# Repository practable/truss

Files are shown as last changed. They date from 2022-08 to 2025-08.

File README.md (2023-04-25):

# truss

## Introduction

The truss remote laboratory has been designed for use with Structural Engineering and Engineering Design courses at the University of Edinburgh. The truss consists of 6 members, each with a full-bridge strain gauge arrangement using two biaxial strain gauges ([Kyowa KFGS-2-120-D16-11](./hw/docs/)). Strain gauge voltages are converted to digital signals using the [HX711 ADC](./hw/docs/) and this [HX711 library](https://www.arduino.cc/reference/en/libraries/hx711-arduino-library/) is used to read and tare the gauges. The truss is loaded using a [linear servo](./hw/docs/). 

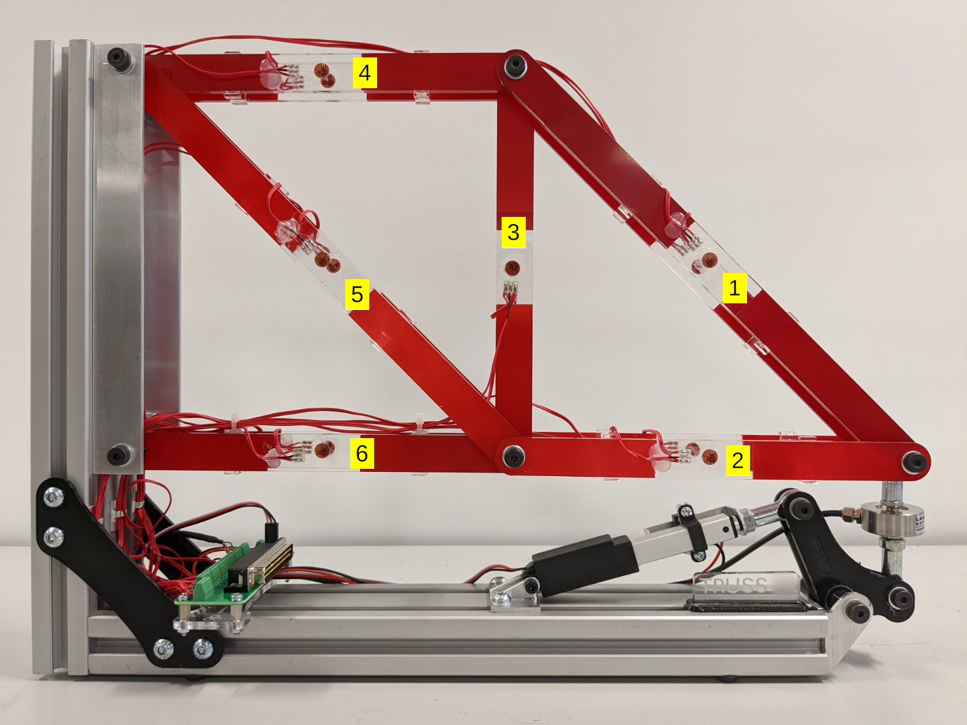
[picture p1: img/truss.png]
truss


## Contents

- [Firmware ./fw](./fw/)
- [Hardware ./hw](./hw/)
- [SBC ./sbc](./sbc/)
- [UI ./ui](./ui/)

## UI

User Interfaces have been designed with Vue3.js and built with Vite. There are currently three distinct versions of the UI ready to build:

- [default](./ui/default/): all data and components available on the user interface.
- [no-force](./ui/no-force/): force data is hidden for student calculation from strain data.
- [open-day](./ui/open-day/): simplified control interface for demonstrations.

## Changing control interface on UI

The differences in the above UI versions amount to very simple changes in the Vue files. 

The load force can be controlled with either a slider or simple buttons (as well experimental versions of a skeuomorphic display and gamepad control). Simply update the `loadControlVersion` parameter in `App.vue`.

```
loadControlVersion: 1,    //0 => input field, 1=> slider, 2=>simulation of physical knob, 3 => direct commands typed, 4 => GamePad, 5 => open day, simple buttons
```

To change whether the load force is displayed or the theoretical strains are available, update the boolean parameters in `src/modules/uiStore.js`:

```
show_force: false,       //should force values be displayed on the UI
show_theory: false,      //should the theoretical values component be available on the UI
```

## Firmware

The truss remote lab has been designed around the Arduino Nano 33 IoT. The firmware uses a state machine with 11 states, including reading, writing, taring and resetting strain gauges and moving the linear actuator. A single microcontroller performs both reading and writing of data. The state machine will remain in the READ state until a user command to change state. Upon performing that state the state machine will return to READ. The required libraries are included [here](./fw/libraries/). 

The firmware sends and receives JSON messages, eg:

Mode control, received from UI through Serial (for all commands see [SerialCommands](./fw/MiniTruss/):

```
{"set": "position", "to": value} 
{"set": "mode", "to": "move"} 
{"set": "mode", "to":"tare_all"} 
```

Sending data to UI through Serial:
```
{"load_cell":"20.0", "gauge_1": "100.0", "gauge_2": "100.0", "gauge_3": "100.0", "gauge_4": "100.0", "gauge_5": "100.0", "gauge_6": "100.0", "state":"1", "pos":"10"}
```

## PCB

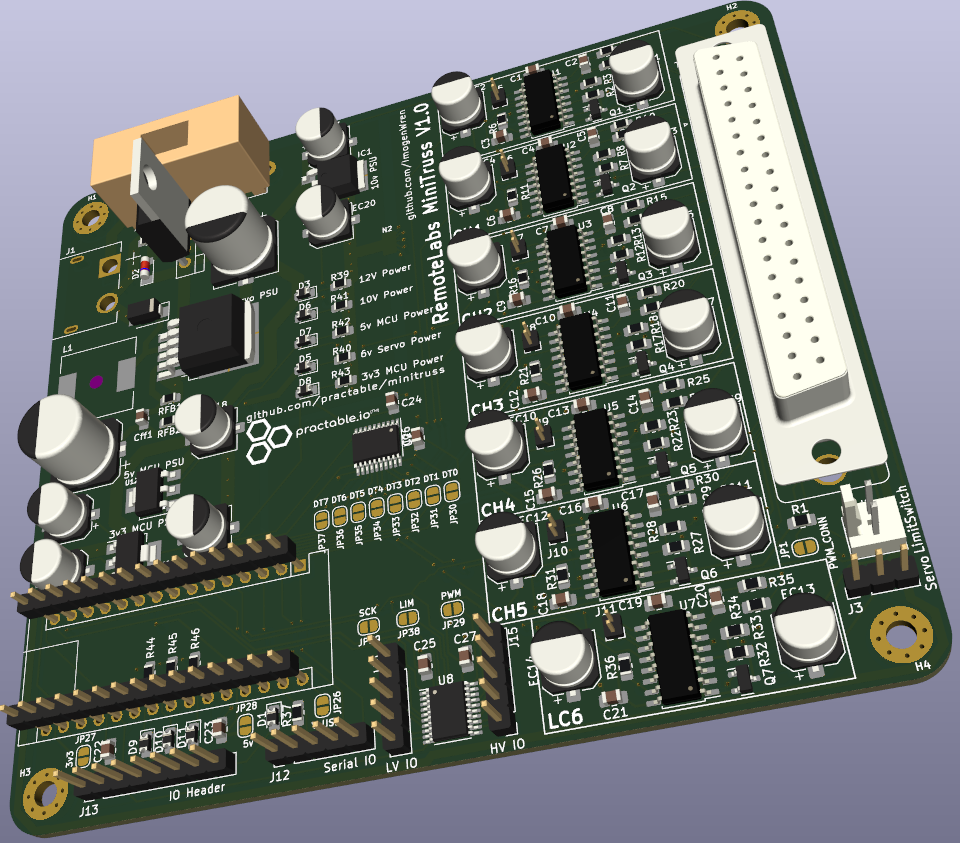
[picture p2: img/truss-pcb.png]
truss-pcb


The PCB requires a 12V input and provides output voltages for different components: 10V (load cell excitation voltage), 6V (linear actuator power) and 5V (strain gauge excitation voltage). Details of jumper requirements for setting up the PCB in different modes will be added (TODO).

## Hardware

linear-actuator

The [Actuonix L16](./hw/docs/Actuonix+L16+Datasheet.pdf) linear actuator uses the custom library LinearServo for setting its position. It has a 50mm stroke length, but is limited in this remote lab to a maximum of 20% extension (providing around 150N of load on the truss).

## Re-calibration procedure

If a strain gauge value no longer reads an acceptable result (within your experimental tolerance) then the scale factor needs to be updated in the firmware.

- Note the value in micro-strain that the gauge is currently reading (current_value)
- Note the current scale factor for that gauge (current_factor)
- Calculate the value that you want it to read based on the load force (new_value)
- new_factor = current_value*current_factor / new_value

Using the debug UI (or any other means of sending a JSON command through Websocket to the experiment): send the new calibration data:

```
{"set":"cal","to":[2.0,2.1,2.2,2.3,2.4,2.5,2.6],"auth":"foo"}
```

Using the auth code that you set up initially.

Then reset to the STARTUP state so that the firmware loads the new calibration data:

```
{"set":"state","to":"STATE_STARTUP"}
```

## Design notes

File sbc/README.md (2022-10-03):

# odroid-truss
How to set up an Odroid to run a truss experiment. 

The process is fairly simple
0. Obtain an eMMC card with Ubuntu 20.04 LTS 
0. Connect Odroid to power, network and a Nano IoT33 
0. Log in to check you have ssh access
0. Edit the sudoers file to allow passwordless sudo
1. Run a configure script on your admin machine
2. Run four ansible playbooks on your admin machine (which set things up on the rpi over ssh)
3. Reboot your Odroid
3. Your experiment should be working

## Abbreviations

- BYOD - Bring Your Own Device
- OS - Operating System
- SBC - single board computer (Raspberry Pi, Odroid, etc)

## Formatting

### Trimming information

`<snip>` is used to denote that line(s) have been removed for clarity

```
something useful
<snip>
other useful stuff
```

#### repo location

`$this_repo` is used to indicate the root of the git repo for clarity in the documentation, and does not actually occur in any of the scripts.

### Indicating where to enter commands?

Code snippets will sometimes clarify which machine they should be run on, if it is not obvious from the context. E.g. your local admin machine:
```
# local
$ <some commands>
```

or on the SBC (via the ssh connection you've established from your local machine). 

```
# sbc
$ <some command>
```

## Prequisites

### Hardware

This is our tested configuration. 

- Odroid C4 
- 32GB eMMC preloaded with ubuntu 20.04 LTS (or a blank eMMC and an adapter so you can image it)
- USB A to micro B cable for arduino
- Arduino Nano IOT33
- USB Webcam (Logitech C920)
- 12V power supply with barrel jack connector
- RJ45 Ethernet connection (avoid WiFi because it is laggy for users)
	
For assembling the full experiment, you will also need some additional items that are outside the scope of this repo:
- Truss PCBs including sensor and connector boards
- Truss hardware (truss, guages, actuator, load cell)
- Experimental tray and 1/6th scale shipping container

### Software

The setup is best done from a linux machine. We have no plans to support commercial operating systems.

- Linux 
   - recommend Ubuntu 20.04 LTS
- Practable's [relay](https://github.com/practable/relay) 
    - ensure the `sessionrelay` and `shellrelay` commands are in your path
    - you may need to rename the commands from `session` to `sessionrelay`, and `shell` to `shellrelay` when you copy them to `/usr/local/bin'.
- Mo templating in bash 
    - see [github](https://github.com/tests-always-included/mo) for installation
    - there are other ways to get mo (e.g. with python) but we don't know if they work, so avoid for now.
- Ansible 
   - Tasks developed with v2.9.17 and python 3.7.4
   - [Installation](https://docs.ansible.com/ansible/latest/installation_guide/intro_installation.html)

### Information

You will need either access tokens or the access secret(s) to your relay(s). Your site administrator for practable will advise. These scripts are written for the case you have the secret. If you have been provided some tokens, you just copy them into `$this_repo/autogenerated` and skip some steps where indicated.

We assume that your relay access secret is the same for all the relays in use, and available at `~/secret/practable.pat`. That way, it's not in the repo.

### Network

You need a wired staging network where unknown devices can obtain an IP address via DHCP. Your admin machine is ideally also in the same subnet as your RPI. If you are at work/university, then you will need to create your own staging network because most institutional networks prevent unknown devices from accessing the wired networks. Without a staging network, you are are stuck in a catch-22 of not knowing enough about the device to get that permission for access to the production network (typically a BYOD network for devices that staff and students might bring in).

Good staging networks: your home network (no re-configuration is needed) or a linux laptop with a wifi connection and an RJ45 dongle (share the wifi to the dongle) - I use one for initial setups and the other for ad-hoc direct connections to experiments during field-testing.

### User environment

#### Mandatory

None listed

## Setup

Overview: The process starts by loading an OS onto an SD card, modifying it to permit `ssh` access, then finishing the setup over an ssh connection. There are a mixture of steps conducted on the SBC

### SBC OS

#### Base Image

Obtain a preloaded eMMC with Ubuntu 20.04 LTS, or image this to your blank eMMC. The most likely looking offical distro is [this](https://odroid.in/ubuntu_22.04lts/C4_HC4/ubuntu-22.04-4.9-minimal-odroid-c4-hc4-20220705.img.xz).  

SSH is enabled by default.

#### Find the IP address of your SBC

Before booting your SBC, you need to figure out the IP addresses of other devices on your network. In the next step, we will be looking for the IP address of the SBC, and it is easier if you already know which devices are NOT the SBC.

First, let's figure out the IP address of the wired ethernet port on your admin machine 
```
$ ip addr 
<snip>
3: enp0s31f6: <BROADCAST,MULTICAST,UP,LOWER_UP> mtu 1500 qdisc fq_codel state UP group default qlen 1000
    link/ether xx:xx:xx:xx:xx:xx brd ff:ff:ff:ff:ff:ff
    inet 192.168.0.46/24 brd 192.168.0.255 scope global dynamic noprefixroute enp0s31f6
       valid_lft 784687sec preferred_lft 784687sec
    inet6 xxxx::xxxx:xxxx:xxxx:xxxx/64 scope link noprefixroute 
       valid_lft forever preferred_lft forever
<snip>
```
Our network card is at 192.168.0.46. The first three number groups matter here. Find all the devices on the same sub-net, using that IP address by set the last number group to `1/24` which is [shorthand](https://www.ietf.org/rfc/rfc1878.txt) for 0-254 (all possible IP in the subnet).
```
$ sudo nmap -sP 192.168.0.1/24
sudo nmap -sP 192.168.0.1/24
Starting Nmap 7.80 ( https://nmap.org ) at 2022-08-25 13:18 BST
Nmap scan report for _gateway (192.168.0.1)
Host is up (0.0016s latency).
MAC Address: xx:xx:xx:xx:xx:xx 
Nmap scan report for 192.168.0.62
Host is up (0.00059s latency).
MAC Address: xx:xx:xx:xx:xx:xx 
Nmap scan report for 192.168.0.52
Host is up (0.036s latency).
MAC Address: xx:xx:xx:xx:xx:xx 
Nmap scan report for 192.168.0.184
Host is up (0.00027s latency).
Nmap done: 256 IP addresses (3 hosts up) 
```

Put the eMMC card on your Odroid, connect the network cable, and power on. Wait about a minute (or repeat until a new device shows up)

```
$ sudo nmap -sP 192.168.0.1/24
sudo nmap -sP 192.168.0.1/24
Starting Nmap 7.80 ( https://nmap.org ) at 2022-08-25 13:20 BST
Nmap scan report for _gateway (192.168.0.1)
Host is up (0.0016s latency).
MAC Address: yy:yy:yy:yy:yy:yy (Arris Group)
Nmap scan report for 192.168.0.29
Host is up (0.032s latency).
MAC Address: xx:xx:xx:xx:xx:xx 
Nmap scan report for 192.168.0.62
Host is up (0.00059s latency).
MAC Address: xx:xx:xx:xx:xx:xx 
Nmap scan report for 192.168.0.52
Host is up (0.036s latency).
MAC Address: xx:xx:xx:xx:xx:xx 
Nmap scan report for 192.168.0.184
Host is up (0.00027s latency).
Nmap done: 256 IP addresses (4 hosts up) 
```
Now you should see a new device. If this step does not work, then the eMMC is corrupt, the network cable/power are disconnected, or the router on your network is not permitting DHCP requests from unknown devices.

In this case the IP address is 192.168.0.29.

Make a note of the MAC address of your SBC so that you can share that with your network administrators at the University - sometimes you must declare the MAC address to be able to access a wired BYOD network.

#### ssh into your SBC

The standard user and password on the odroid image is usually `odroid/odroid`

On your machine, open a terminal
```
$ ssh pi@192.168.0.29 #change to whatever IP you found in previous step

The authenticity of host '192.168.0.29 (192.168.0.29)' can't be established.
ECDSA key fingerprint is SHA256:/0jZ9w8zL4h94rojSnSQ0Yewv5G8qK2AjCod/09pBkE.
Are you sure you want to continue connecting (yes/no/[fingerprint])? yes
Warning: Permanently added '192.168.0.29' (ECDSA) to the list of known hosts.
pi@192.168.0.29's password: <--- enter the password here 

```
Then you should see something like this:

```
Welcome to Ubuntu 20.04 LTS (GNU/Linux 4.9.218-13 aarch64)

 * Documentation:  https://help.ubuntu.com
 * Management:     https://landscape.canonical.com
 * Support:        https://ubuntu.com/advantage

 * Super-optimized for small spaces - read how we shrank the memory
   footprint of MicroK8s to make it the smallest full K8s around.

   https://ubuntu.com/blog/microk8s-memory-optimisation

607 updates can be installed immediately.
426 of these updates are security updates.
To see these additional updates run: apt list --upgradable

Last login: Fri Jul  1 20:11:11 2022 from 192.168.0.46
odroid@odroid:~$  
```

##### Password

Change the password 

```
$ passwd
```

Ideally we would also set up ssh certificates but this is a future step.

##### Sudo

Set up passwordless sudo

```
#sbc
sudo visudo 
```

At the end of the file add

```
odroid ALL=(ALL) NOPASSWD: ALL
```

Save the file. The default editor might be joe, in which case you hit `^KX` (i.e. hold CTRL, type KX, release CTRL) to save. Assuming you made no errors, you will see:

```
File /etc/sudoers.tmp saved
```

Once the sudoers file is edited, you can check it by logging back out and back in, then trying 

```
$ sudo su
root@odroid:/home/odroid# 
```

which should work without needing a password.

You can now exit the session - we will do the next steps using ansible.

```
# sbc
$ exit
```

### SBC software and configuration

We need to generate some configuration files that are customised to your experiment. Your local admin for the practable system will advise on any naming conventions that apply at your site, as well as providing the relay key(s) which you need. 

#### Ansible hosts file

We need to let ansible know about this host.

```
sudo nano /etc/ansible/hosts
```
Add in a section like this (or modify an existing section if you have one)

```
<snip>
[truss]
trus00 ansible_host=192.168.0.29 practable_label=trus00

[truss:vars]
ansible_connection=ssh
ansible_user=odroid
ansible_password=somepassword
<snip>

```

#### Practable connections

We need to configure routing and tokens for the video, data, shell, and shell2 connections. There are scripts provided to help you. They put files into `$this_repo./autogenerated`

Create the configuration files we need, assuming we are using the standard practable relay URLs.

```
#local
cd scripts
./configure trus 00 00 https://relay-access.practable.io https://shell-access.practable.io https://shell-access2.practable.io
```

##### Session

Now we can run our ansible playbooks - these each take some time, so get the kettle ready. It's nearly as fast doing multiple machines, because the playbooks are run in parallel. There is no need to do each SBC separately one after another.

```
#local
cd playbooks
ansible-playbook prepare.yml
ansible-playbook install-session.yml
ansible-playbook install-shell.yml
ansible-playbook install-firmware.yml
```

If those commands go smoothly, then you are done with the install. If not, then re-run the playbook with the issue, before moving on. If that fails, check out the troubleshooting guide below.

## Checking the installation

Go to the booking page link the adminstrator gave you, and you should be able to access/control the experiment. 

## Troubleshooting

If things are not working right, then you might be able to fix them by troubleshooting. 

### First playbook fails

If you get this error, just redo the playbook. It's down to the python interpreter not being picked up after installation in a previous step.

```
TASK [Remove any existing go files] *******************************************************************************************************************
fatal: [trus02]: FAILED! => {"changed": false, "module_stderr": "/bin/sh: 1: /usr/bin/python: not found\n", "module_stdout": "", "msg": "The module failed to execute correctly, you probably need to set the interpreter.\nSee stdout/stderr for the exact error", "rc": 127}
```

### No DHCP

This is usually caused by 
- eMMC corrupt 
- network administrator is unaware of the MAC address of the wired network port on the SBC

### No SSH connection

For odroid, `sshd` is enabled by default, so you will need to use a keyboard and mouse to re-enable, or reflash (depending on whether there is anything on the eMMC you want to keep).

### Remote host identification has changed

If you work with a lot of experiments, sooner or later an old IP address on your staging network will be re-assigned to a new experiment you are setting up, and then you will see something like this:

```
@@@@@@@@@@@@@@@@@@@@@@@@@@@@@@@@@@@@@@@@@@@@@@@@@@@@@@@@@@@
@    WARNING: REMOTE HOST IDENTIFICATION HAS CHANGED!     @
@@@@@@@@@@@@@@@@@@@@@@@@@@@@@@@@@@@@@@@@@@@@@@@@@@@@@@@@@@@
IT IS POSSIBLE THAT SOMEONE IS DOING SOMETHING NASTY!
Someone could be eavesdropping on you right now (man-in-the-middle attack)!
It is also possible that a host key has just been changed.
The fingerprint for the ECDSA key sent by the remote host is
SHA256:/0jZ9w8zL4h94rojSnSQ0Yewv5G8qK2AjCod/09pBkE.
Please contact your system administrator.
Add correct host key in /home/tim/.ssh/known_hosts to get rid of this message.
Offending ECDSA key in /home/tim/.ssh/known_hosts:178
  remove with:
  ssh-keygen -f "/home/tim/.ssh/known_hosts" -R "192.168.0.184"
ECDSA host key for 192.168.0.184 has changed and you have requested strict checking.
Host key verification failed.
```

Simply run the suggested command, and then carry on where you left off with trying to connect over `ssh`. The command is unique each time it happens (you're overwriting an entry in the known-hosts file so it must correspond to the host causing the problem _this_ time). E.g.

```
$ssh-keygen -f "/home/tim/.ssh/known_hosts" -R "192.168.0.184"

# Host 192.168.0.184 found: line 178
/home/tim/.ssh/known_hosts updated.
Original contents retained as /home/tim/.ssh/known_hosts.old
```

### Check the OS
If you're not sure if you have the right OS for the ansible scripts, you can check. For this experiment, you should see something like this

```
$ uname -a
Linux odroid 4.9.218-13 #1 SMP PREEMPT Tue Apr 21 20:02:01 UTC 2020 aarch64 aarch64 aarch64 GNU/Linux
```

### Ansible cannot reach SBC

If you are having trouble connecting via ansible, following the guidance on verbose logging [here](https://docs.ansible.com/ansible/latest/network/user_guide/network_debug_troubleshooting.html)

You might find you've got the format of the /etc/ansible/hosts incorrect (e.g. didn't name the vars section correctly, got the password wrong etc).

### ttyACM0 Device not found 

If you get this error, reboot the SBC and try again. If the error persists, check which device name it has been assigned (`/dev/ttyACM0` is expected for Nano 33 IOT)
```
#rpi
lsusb
dmesg | tail
```

### Error with sudo / sudoers

If you made an error, you might see something like this
```
>>> /etc/sudoers: syntax error near line 26 <<<
What now? 
```
In which case, hit `e` to go back to the editor and correct the mistake.

#### Direct editing error

Editing the sudoers file directly can lock you out of running commands as sudo, if you make an error. Recovering it is [straightforward](https://askubuntu.com/questions/73864/how-to-modify-an-invalid-etc-sudoers-file).

Ali Tou says:
"When this happens to a non-GUI system (your production server, maybe) the pkexec fails with this error message:

```
polkit-agent-helper-1: error response to PolicyKit daemon: GDBus.Error:org.freedesktop.PolicyKit1.Error.Failed: No session for cookie
==== AUTHENTICATION FAILED ===
Error executing command as another user: Not authorized
```
In this situation, using `pkttyagent` can be helpful. If you want to remove a corrupted file in `sudoers.d` directory, use this:

```
pkttyagent -p $(echo $$) | pkexec rm /etc/sudoers.d/FILENAME
```

If you want to recover the default `/etc/sudoers`, you can use [this gist](https://gist.github.com/alitoufighi/679304d9585304075ba1ad93f80cce0e) to copy the default configurations, putting it in a non-root accessed place (e.g. your $HOME). Then, you can overwrite your sudoers file:

```
pkttyagent -p $(echo $$) | pkexec cp ~/sudoers /etc/sudoers
```
NOTE: Using this approach, after running your command, probably your access to the shell will be gone. But I'm sure losing one shell session is much better than losing your server! (According to the manpage, this is the normal behavior: When its services are no longer needed, the process can be killed.)

End of Answer from Ali Tou

In short, create a file `~/sudoers` with the following contents:

```
#
# This file MUST be edited with the 'visudo' command as root.
#
# Please consider adding local content in /etc/sudoers.d/ instead of
# directly modifying this file.
#
# See the man page for details on how to write a sudoers file.
#
Defaults	env_reset
Defaults	mail_badpass
Defaults	secure_path="/usr/local/sbin:/usr/local/bin:/usr/sbin:/usr/bin:/sbin:/bin:/snap/bin"

# Host alias specification

# User alias specification

# Cmnd alias specification

# User privilege specification
root	ALL=(ALL:ALL) ALL

# Members of the admin group may gain root privileges
%admin ALL=(ALL) ALL

# Allow members of group sudo to execute any command
%sudo	ALL=(ALL:ALL) ALL

# See sudoers(5) for more information on "#include" directives:

#includedir /etc/sudoers.d

```

Then run this command:
```
pkttyagent -p $(echo $$) | pkexec cp ~/sudoers /etc/sudoers
```

It should say
```
==== AUTHENTICATING FOR org.freedesktop.policykit.exec ===
Authentication is needed to run `/bin/cp' as the super user
Authenticating as: ,,, (odroid)
Password: 
==== AUTHENTICATION COMPLETE ===
```

At which point, I used a Ctrl-C to get back to the shell. `sudo` now works as expected:

```
odroid@odroid:~$ sudo su
root@odroid:/home/odroid# 
```

### FFMPEG

FFMPEG dependencies can cause issues, and `apt` is better at resolving them than `apt-get`. Should issues occur in future, consider trying something similar to the trick we use successfully so far: is issuing `sudo apt install libsdl2-2.0-0` first to get the right version of the dependency. Note the use of `apt`, not `apt-get`.  `apt-get` wants to install 2.0.8, while `apt` can install the 2.0.10 that `ffmpeg` needs. 

#### Manual token updates

If you want to do a manual token update, then use the configure scripts to autogenerate the token.

Rather than scp, which cannot be done on the shell relay for now, you should do as follows

- log into the odroid
- cat the relevant token in your autogen directory
- sudo rm /etc/practable/data.token
sudo nano /etc/practable/data.token
- paste in your token contents (mind only one line, and don't delete last char when removing last line, check last char against original
- repeat process for video.token
- sudo systemctl restart session-rules

then check getSessionStats.sh as usual

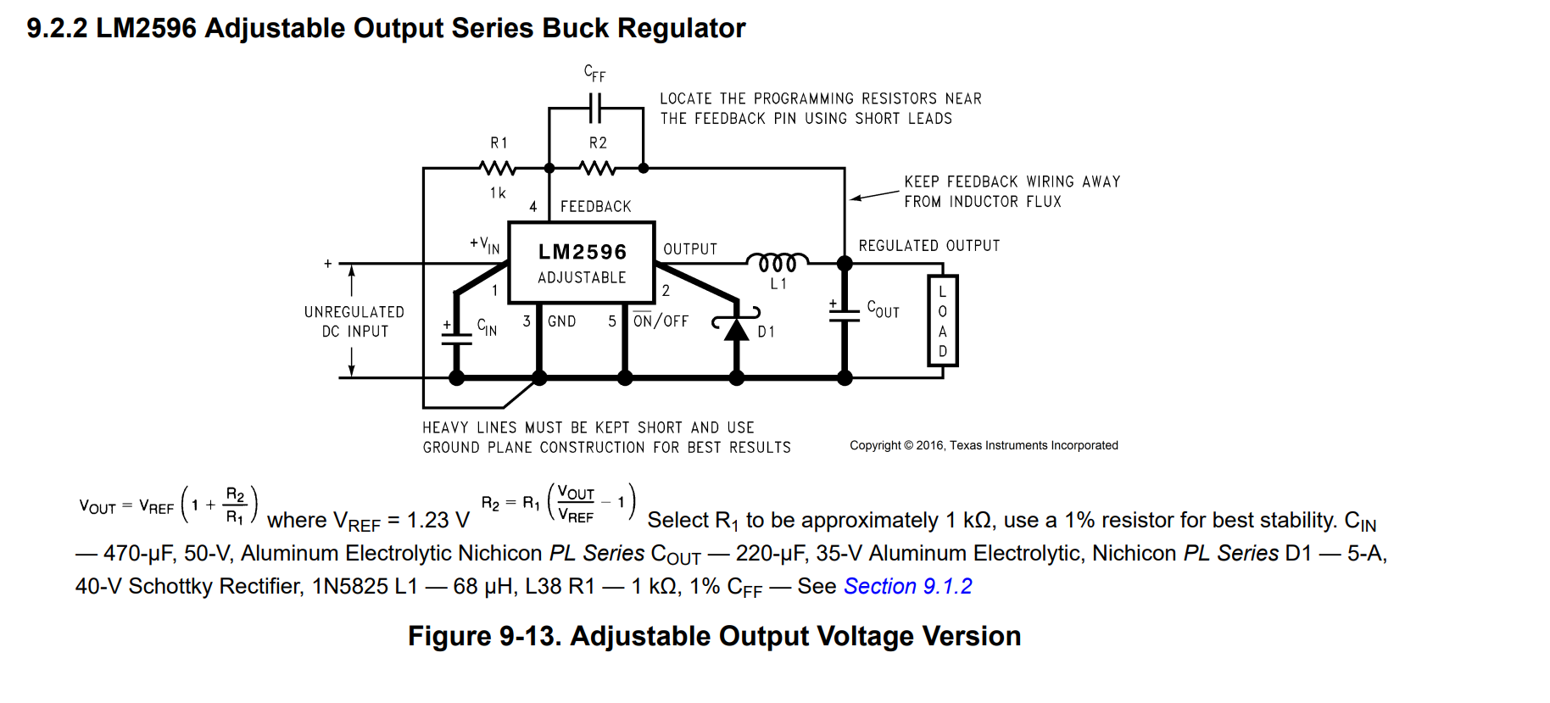
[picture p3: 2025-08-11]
mini-truss-pcb/Documentation/Buck converter schematic.png

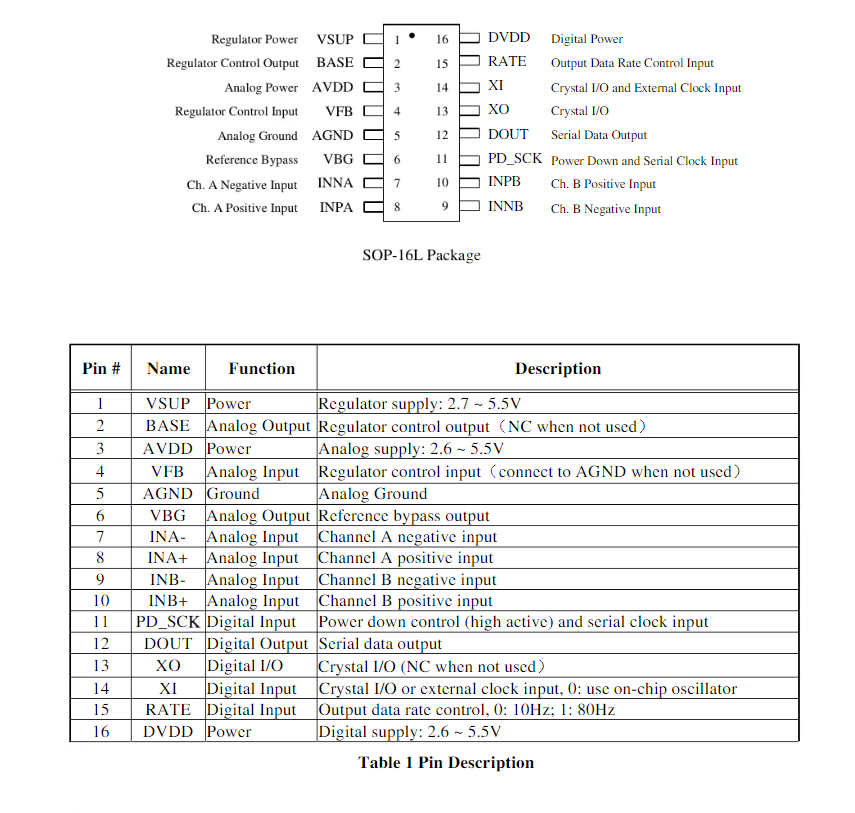
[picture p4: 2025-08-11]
mini-truss-pcb/Documentation/HX711 pinout.png

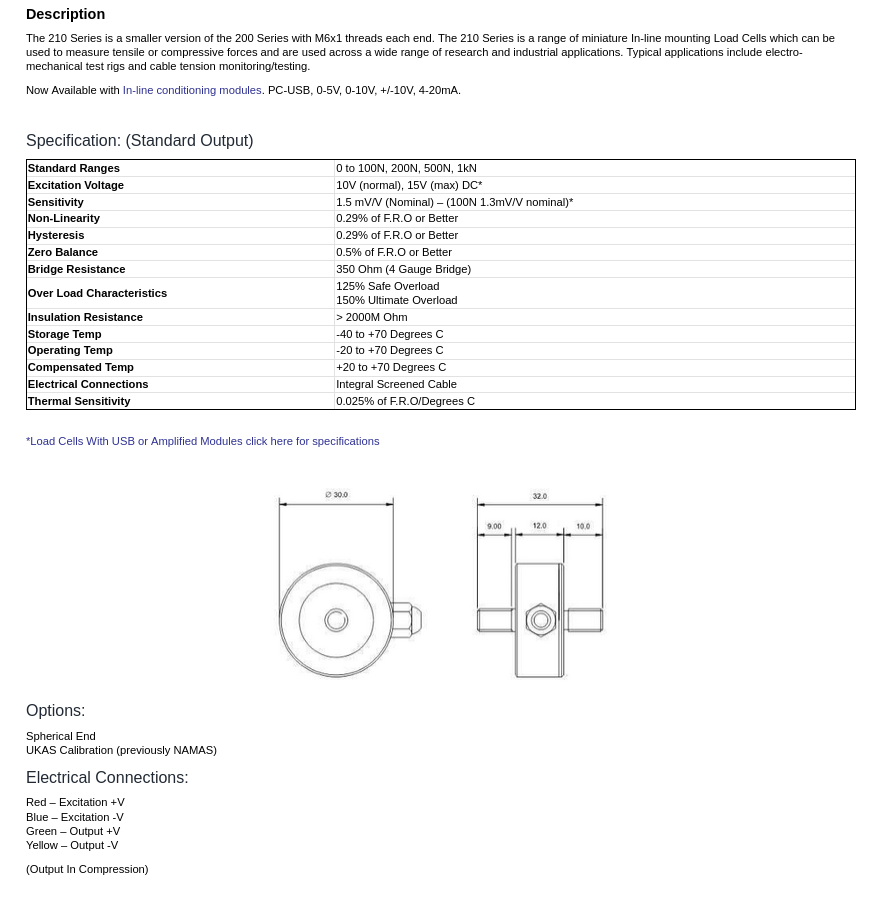
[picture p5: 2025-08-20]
hw/docs/load-cell.png

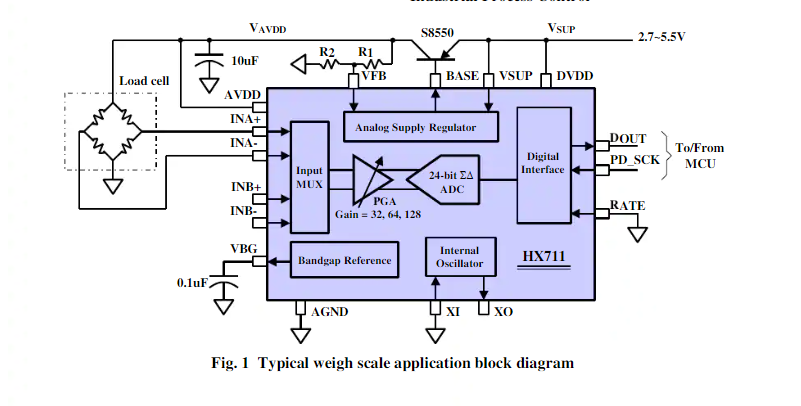
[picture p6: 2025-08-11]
mini-truss-pcb/Documentation/HX711 Application Circuit.png

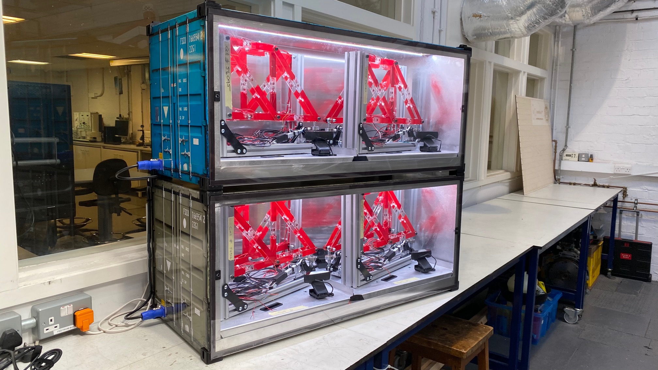
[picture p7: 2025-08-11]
mini-truss-pcb/Documentation/Finished Product Photos/Truss Containers 2.png

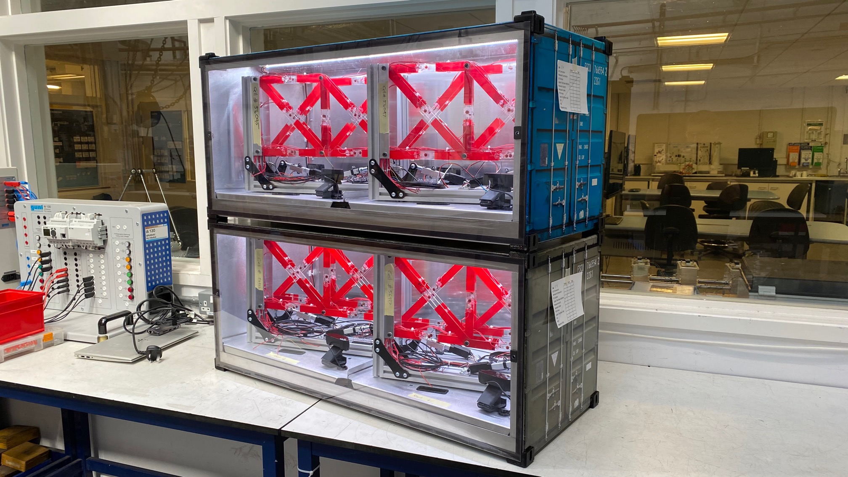
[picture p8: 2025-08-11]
mini-truss-pcb/Documentation/Finished Product Photos/Truss Containers.png

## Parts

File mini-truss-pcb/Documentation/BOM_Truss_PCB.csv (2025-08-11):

Source: | C:\Users\dheard\Documents\KiCad\Projects\truss_PCB\truss_PCB.kicad_sch
Date: | 07/07/2022 15:09
Tool: | Eeschema (6.0.0)
Generator: | C:\Program Files\KiCad\6.0\bin\scripting\plugins/bom_csv_grouped_by_value_with_fp.py
Component Count: | 191
Ref | Qnty | Value | Cmp name | Footprint | Description | Vendor
A1, | 1 | Arduino_Nano_v3.x | Arduino_Nano_v3.x | Module:Arduino_Nano | Arduino Nano v3.x
C1, C2, C3, C4, C5, C6, C7, C8, C9, C10, C11, C12, C13, C14, C15, C16, C17, C18, C19, C20, C21, C22, C23, C24, C25, C26, C27, | 27 | 100n | cap_film_0805 | Capacitor_SMD:C_0805_2012Metric_Pad1.18x1.45mm_HandSolder | Unpolarized capacitor
C28, | 1 | 680u | 100u | Capacitor_SMD:CP_Elec_10x10 | Polarized capacitor
Cff1, | 1 | 3n3 | cap_film_0805 | Capacitor_SMD:C_0805_2012Metric_Pad1.18x1.45mm_HandSolder | Unpolarized capacitor
D1, D9, D10, D11, | 4 | LED | LED_0805_smd | Diode_SMD:D_0805_2012Metric_Pad1.15x1.40mm_HandSolder | Light emitting diode
D2, | 1 | BZV55B9V1 | BZV55B9V1 | Diode_SMD:D_MiniMELF | 9.1V, 500mW, 2%, Zener diode, MiniMELF
D3, | 1 | 12V Power | LED_0805_smd | Diode_SMD:D_0805_2012Metric_Pad1.15x1.40mm_HandSolder | Light emitting diode
D4, | 1 | 1N5821 | 1N5821 | Diode_SMD:D_SMA | 30V 3A Schottky Barrier Rectifier Diode, DO-201AD
D5, | 1 | 6v Servo Power | LED_0805_smd | Diode_SMD:D_0805_2012Metric_Pad1.15x1.40mm_HandSolder | Light emitting diode
D6, | 1 | 10V Power | LED_0805_smd | Diode_SMD:D_0805_2012Metric_Pad1.15x1.40mm_HandSolder | Light emitting diode
D7, | 1 | 5v MCU Power | LED_0805_smd | Diode_SMD:D_0805_2012Metric_Pad1.15x1.40mm_HandSolder | Light emitting diode
D8, | 1 | 3v3 MCU Power | LED_0805_smd | Diode_SMD:D_0805_2012Metric_Pad1.15x1.40mm_HandSolder | Light emitting diode
EC1, EC2, EC3, EC4, EC5, EC6, EC7, EC8, EC9, EC10, EC11, EC12, EC13, EC14, EC20, EC21, EC22, | 17 | 10u | 22u | Capacitor_SMD:CP_Elec_6.3x5.9 | Polarized capacitor
EC15, | 1 | 100u | 100u | Capacitor_SMD:CP_Elec_10x10 | Polarized capacitor
EC17, EC18, EC19, | 3 | 22u | 22u | Capacitor_SMD:CP_Elec_6.3x5.9 | Polarized capacitor
F1, | 1 | 3A | Fuse | Fuse:Fuseholder_Cylinder-5x20mm_Stelvio-Kontek_PTF78_Horizontal_Open | Fuse
IC1, | 1 | BAJ0BC0FP-E2 | BAJ0BC0FP-E2 | Package_TO_SOT_SMD:TO-252-2 | LDO Voltage Regulators IC LDO 1A 10V
J1, | 1 | XT60_60A_male | XT60_60A_male | Connector_AMASS:AMASS_XT60PW-M | Generic connector, single row, 01x02, script generated (kicad-library-utils/schlib/autogen/connector/)
J2, | 1 | LimitSwitch | 2pin_molex_2.54mm_male | Connector_Molex:Molex_KK-254_AE-6410-02A_1x02_P2.54mm_Vertical | Generic connector, single row, 01x02, script generated (kicad-library-utils/schlib/autogen/connector/)
J3, | 1 | Servo | Conn_01x03_Male | Connector_PinHeader_2.54mm:PinHeader_1x03_P2.54mm_Vertical | Generic connector, single row, 01x03, script generated (kicad-library-utils/schlib/autogen/connector/)
J4, | 1 | Truss Connection | DB37_Female_MountingHoles | Connector_Dsub:DSUB-37_Female_Vertical_P2.77x2.84mm_MountingHoles | 37-pin female D-SUB connector, Mounting Hole
L1, | 1 | 33uH | L | Inductor_SMD:L_12x12mm_H8mm | Inductor
Q1, Q2, Q3, Q4, Q5, Q6, Q7, | 7 | BC807 | BC807 | Package_TO_SOT_SMD:SOT-23 | 0.8A Ic, 45V Vce, PNP Transistor, SOT-23
Q8, | 1 | IRF5305_PBF | IRF5305_PBF | Package_TO_SOT_THT:TO-220-3_Vertical | -31A Id, -55V Vds, Single P-Channel HEXFET Power MOSFET, 60mOhm Ron, TO-220AB
R1, R6, R11, R16, R21, R26, R31, R36, R39, | 9 | 10k | Resistor_0805 | Resistor_SMD:R_0805_2012Metric_Pad1.20x1.40mm_HandSolder | Resistor
R2, R7, R12, R17, R22, R27, R32, | 7 | 12k | Resistor_0805 | Resistor_SMD:R_0805_2012Metric_Pad1.20x1.40mm_HandSolder | Resistor
R3, R8, R13, R18, R23, R28, R33, | 7 | 33k | Resistor_0805 | Resistor_SMD:R_0805_2012Metric_Pad1.20x1.40mm_HandSolder | Resistor
R4, R5, R9, R10, R14, R15, R19, R20, R24, R25, R29, R30, R34, R35, | 14 | 100r | Resistor_0805 | Resistor_SMD:R_0805_2012Metric_Pad1.20x1.40mm_HandSolder | Resistor
R37, R40, R42, R44, R45, R46, | 6 | 1k | Resistor_0805 | Resistor_SMD:R_0805_2012Metric_Pad1.20x1.40mm_HandSolder | Resistor
R38, R43, | 2 | 330r | Resistor_0805 | Resistor_SMD:R_0805_2012Metric_Pad1.20x1.40mm_HandSolder | Resistor
R41, | 1 | 8k2 | Resistor_0805 | Resistor_SMD:R_0805_2012Metric_Pad1.20x1.40mm_HandSolder | Resistor
RFB1, | 1 | 860r | Resistor_0805 | Resistor_SMD:R_0805_2012Metric_Pad1.20x1.40mm_HandSolder | Resistor
RFB2, | 1 | 3k3 | Resistor_0805 | Resistor_SMD:R_0805_2012Metric_Pad1.20x1.40mm_HandSolder | Resistor
U1, U2, U3, U4, U5, U6, U7, | 7 | HX711 | HX711_24bit_ADC_Strain_Gauge_Driver | Package_SO:SOP-16_4.55x10.3mm_P1.27mm | Â±6A Bidirectional, Hall-Effect Current Sensor, Latched Fault, +3.3V to +5.0V supply, 151mV/A @ +5.0V, SOIC-16W
U8, U9, | 2 | TXS0108EPW | TXS0108EPW | Package_SO:TSSOP-20_4.4x6.5mm_P0.65mm | Bidirectional level-shifting voltage translator, TSSOP-20
U11, | 1 | LM2596S-ADJ | LM2596S-ADJ | Package_TO_SOT_SMD:TO-263-5_TabPin3 | Adjustable 3A Step-Down Voltage Regulator, TO-263
U12, | 1 | AMS1117-5.0 | AMS1117-5.0 | Package_TO_SOT_SMD:SOT-223-3_TabPin2 | 1A Low Dropout regulator, positive, 5.0V fixed output, SOT-223
U13, | 1 | AMS1117-3.3 | AMS1117-3.3 | Package_TO_SOT_SMD:SOT-223-3_TabPin2 | 1A Low Dropout regulator, positive, 3.3V fixed output, SOT-223

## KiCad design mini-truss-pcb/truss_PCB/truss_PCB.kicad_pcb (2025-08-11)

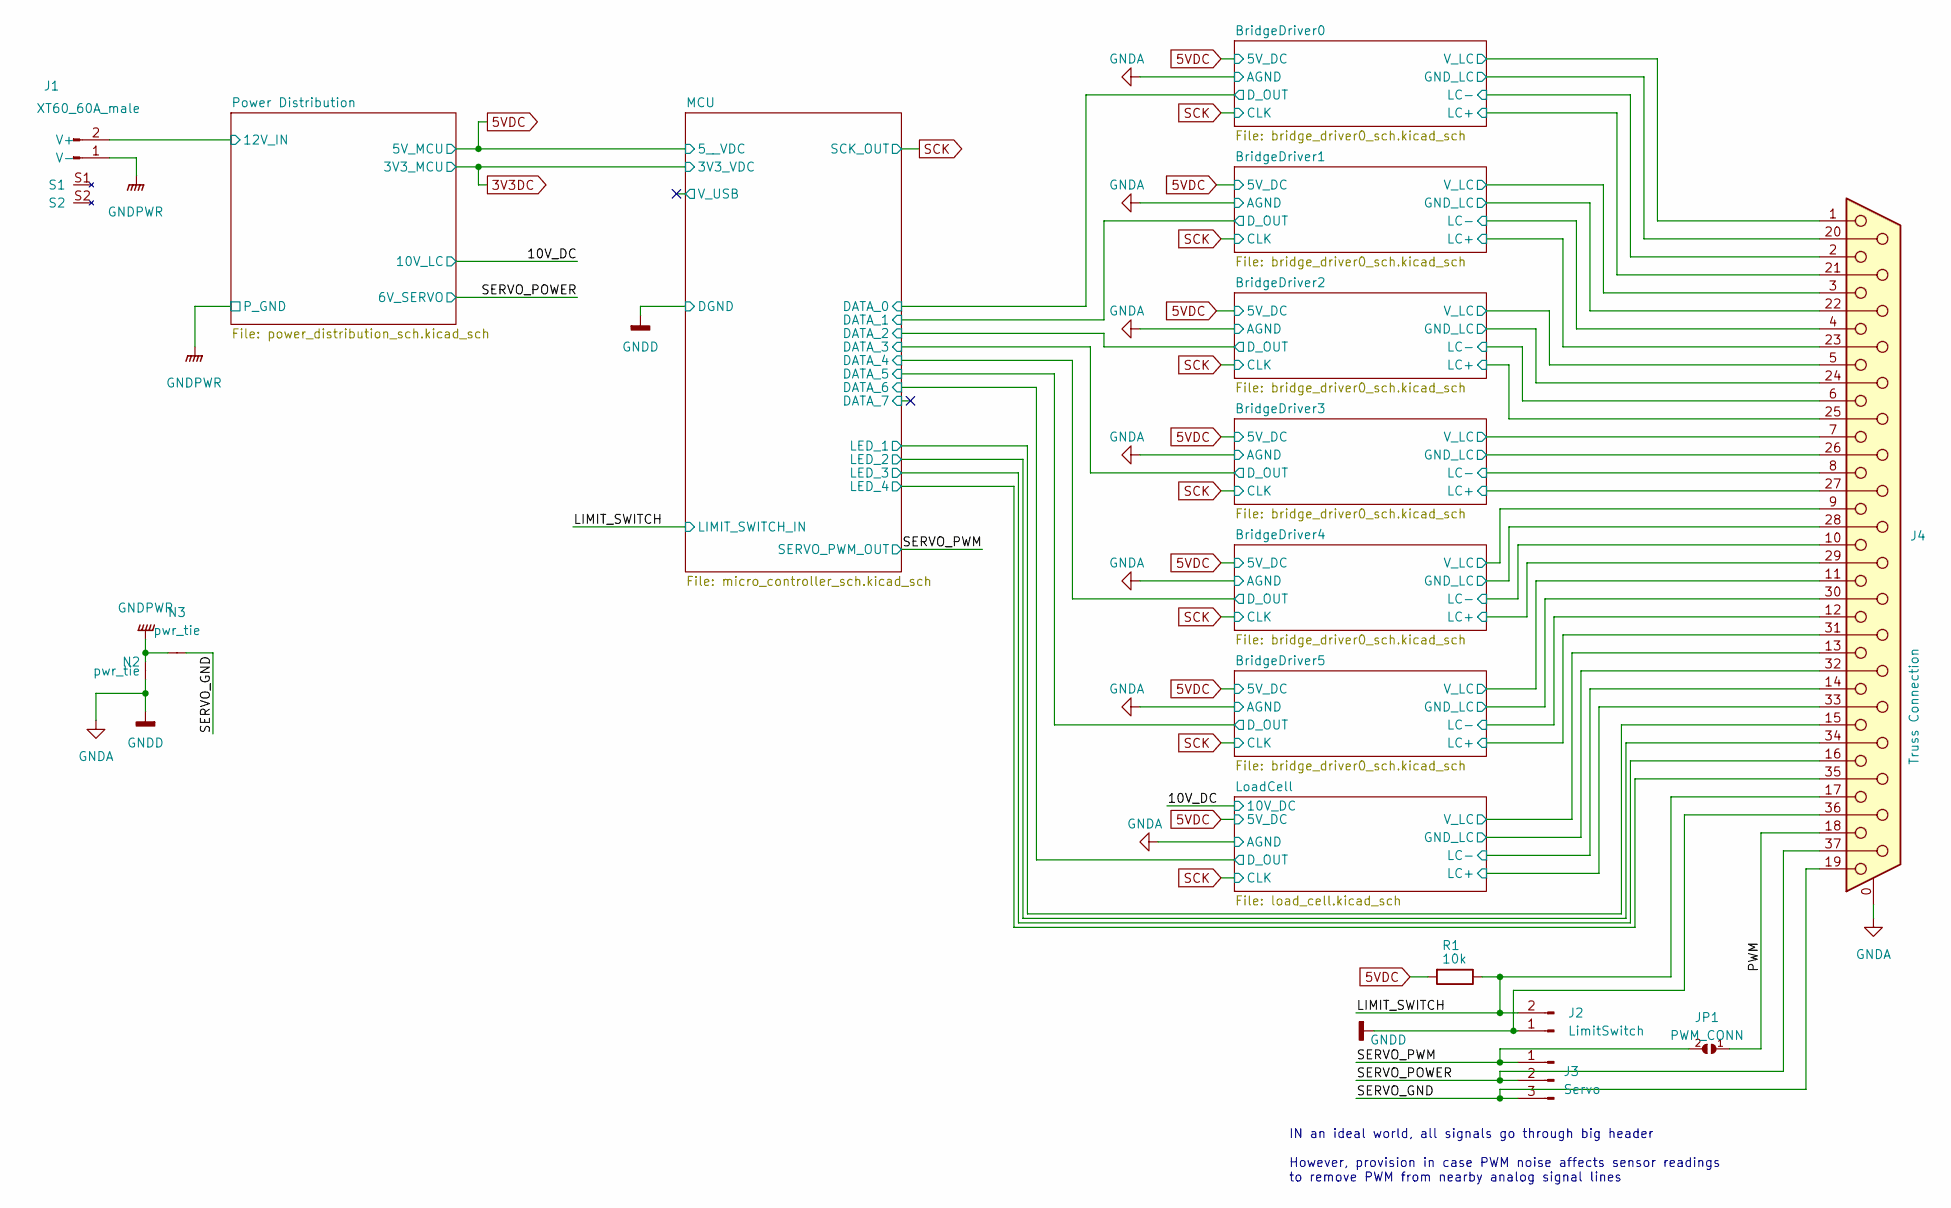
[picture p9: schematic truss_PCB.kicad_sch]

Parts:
J1: XT60_60A_male; AMASS_XT60PW-M
J2: LimitSwitch; Molex_KK-254_AE-6410-02A_1x02_P2.54mm_Vertical
J3: Servo; PinHeader_1x03_P2.54mm_Vertical
J4: Truss Connection; DSUB-37_Female_Vertical_P2.77x2.84mm_MountingHoles
JP1: PWM_CONN; SolderJumper-2_P1.3mm_Open_RoundedPad1.0x1.5mm
N2, N3: pwr_tie; NetTie-8-15A_1oz_2oz
R1: 10k; R_0805_2012Metric_Pad1.20x1.40mm_HandSolder

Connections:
5VDC: R1.2; also elsewhere on the board
/BridgeDriver0/LC+: J4.21; also elsewhere on the board
/BridgeDriver0/LC-: J4.2; also elsewhere on the board
/BridgeDriver0/V_LC: J4.1; also elsewhere on the board
/BridgeDriver1/LC+: J4.23; also elsewhere on the board
/BridgeDriver1/LC-: J4.4; also elsewhere on the board
/BridgeDriver1/V_LC: J4.3; also elsewhere on the board
/BridgeDriver2/LC+: J4.25; also elsewhere on the board
/BridgeDriver2/LC-: J4.6; also elsewhere on the board
/BridgeDriver2/V_LC: J4.5; also elsewhere on the board
/BridgeDriver3/LC+: J4.27; also elsewhere on the board
/BridgeDriver3/LC-: J4.8; also elsewhere on the board
/BridgeDriver3/V_LC: J4.7; also elsewhere on the board
/BridgeDriver4/LC+: J4.29; also elsewhere on the board
/BridgeDriver4/LC-: J4.10; also elsewhere on the board
/BridgeDriver4/V_LC: J4.9; also elsewhere on the board
/BridgeDriver5/LC+: J4.31; also elsewhere on the board
/BridgeDriver5/LC-: J4.12; also elsewhere on the board
/BridgeDriver5/V_LC: J4.11; also elsewhere on the board
/LIMIT_SWITCH: J2.2, J4.17, R1.1; also elsewhere on the board
/LoadCell/LC+: J4.33; also elsewhere on the board
/LoadCell/LC-: J4.14; also elsewhere on the board
/LoadCell/V_LC: J4.13; also elsewhere on the board
/MCU/LED_2: J4.34; also elsewhere on the board
/MCU/LED_3: J4.16; also elsewhere on the board
/MCU/LED_4: J4.35; also elsewhere on the board
/MCU/SPARE_0: J4.15; also elsewhere on the board
/PWM: J4.18, JP1.1 (A)
/Power Distribution/12V_IN: J1.2 (V+); also elsewhere on the board
/SERVO_GND: J3.3, J4.19, N3.2 (C)
/SERVO_POWER: J3.2, J4.37; also elsewhere on the board
/SERVO_PWM: J3.1, JP1.2 (B); also elsewhere on the board
GNDA: J2.1, J4.0 (PAD), J4.20, J4.22, J4.24, J4.26, J4.28, J4.30, J4.32, J4.36, N2.1 (A); also elsewhere on the board
GNDPWR: J1.1 (V-), N2.2 (C), N3.1 (A); also elsewhere on the board

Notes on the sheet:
IN an ideal world, all signals go through big header However, provision in case PWM noise affects sensor readings to remove PWM from nearby analog signal lines

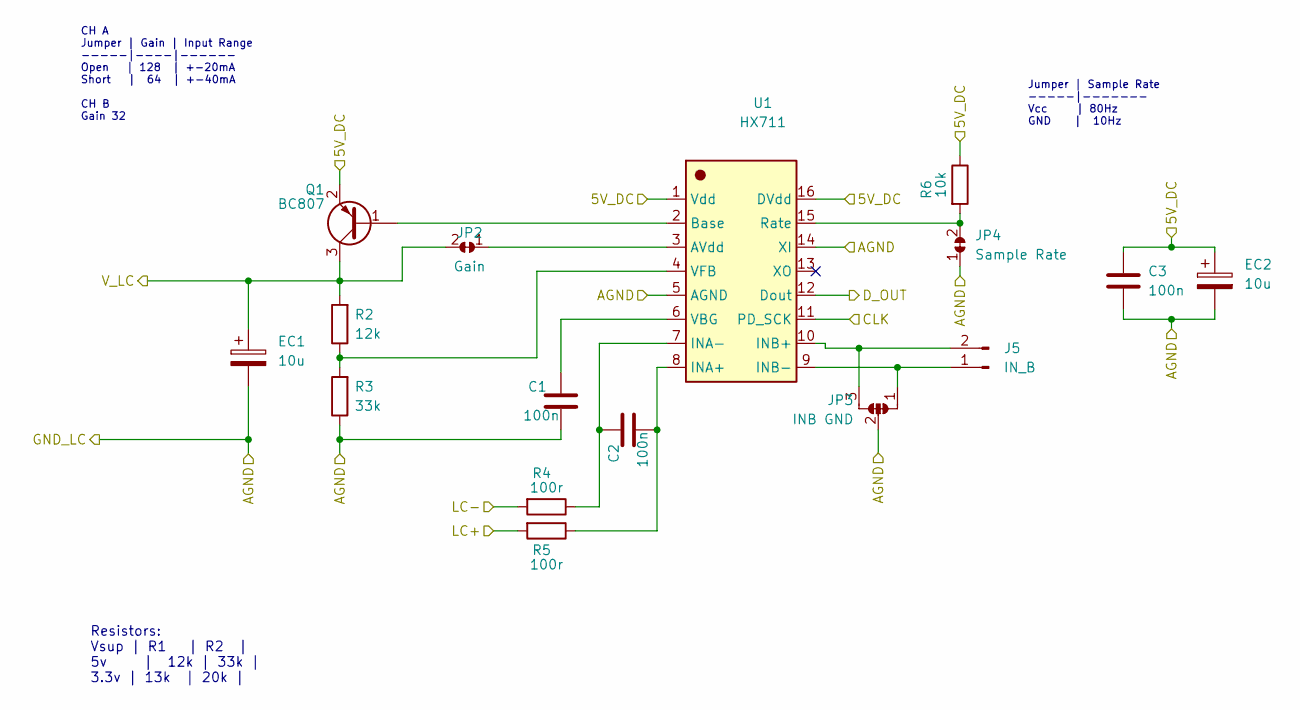
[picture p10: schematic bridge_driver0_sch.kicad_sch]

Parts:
C1, C2, C3: 100n; C_0805_2012Metric_Pad1.18x1.45mm_HandSolder
EC1, EC2: 10u; CP_Elec_6.3x5.9
J5: IN_B; PinHeader_1x02_P1.27mm_Vertical
JP2: Gain; SolderJumper-2_P1.3mm_Bridged_RoundedPad1.0x1.5mm
JP3: INB GND; SolderJumper-3_P1.3mm_Bridged12_RoundedPad1.0x1.5mm_DoubleJ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
JP4: Sample Rate; SolderJumper-2_P1.3mm_Bridged_RoundedPad1.0x1.5mm
Q1: BC807; SOT-23
R2: 12k; R_0805_2012Metric_Pad1.20x1.40mm_HandSolder
R3: 33k; R_0805_2012Metric_Pad1.20x1.40mm_HandSolder
R4, R5: 100r; R_0805_2012Metric_Pad1.20x1.40mm_HandSolder
R6: 10k; R_0805_2012Metric_Pad1.20x1.40mm_HandSolder
U1: HX711; SOP-16_4.55x10.3mm_P1.27mm

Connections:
5VDC: C3.1, EC2.1, Q1.2 (E), R6.1, U1.1 (Vdd), U1.16 (DVdd); also elsewhere on the board
/BridgeDriver0/D_OUT: U1.12 (Dout); also elsewhere on the board
/BridgeDriver0/LC+: R5.2; also elsewhere on the board
/BridgeDriver0/LC-: R4.2; also elsewhere on the board
/BridgeDriver0/V_LC: EC1.1, JP2.2 (B), Q1.3 (C), R2.2; also elsewhere on the board
GNDA: C1.2, C3.2, EC1.2, EC2.2, JP3.2 (C), JP4.1 (A), R3.1, U1.5 (AGND), U1.14 (XI); also elsewhere on the board
unnamed: C1.1, U1.6 (VBG)
unnamed: C2.1, R4.1, U1.7 (INA-)
unnamed: C2.2, R5.1, U1.8 (INA+)
unnamed: J5.1, JP3.1 (A), U1.9 (INB-)
unnamed: J5.2, JP3.3 (B), U1.10 (INB+)
unnamed: JP2.1 (A), U1.3 (AVdd)
unnamed: JP4.2 (B), R6.2, U1.15 (Rate)
unnamed: Q1.1 (B), U1.2 (Base)
unnamed: R2.1, R3.2, U1.4 (VFB)
SCK: U1.11 (PD_SCK); also elsewhere on the board

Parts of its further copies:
C4, C5, C6, C7, C8, C9, C10, C11, C12, C13, C14, C15, C16, C17, C18: 100n; C_0805_2012Metric_Pad1.18x1.45mm_HandSolder
EC3, EC4, EC5, EC6, EC7, EC8, EC9, EC10, EC11, EC12: 10u; CP_Elec_6.3x5.9
J6, J7, J8, J9, J10: IN_B; PinHeader_1x02_P1.27mm_Vertical
JP5, JP8, JP11, JP14, JP17: Gain; SolderJumper-2_P1.3mm_Bridged_RoundedPad1.0x1.5mm
JP6, JP9, JP12, JP15, JP18: INB GND; SolderJumper-3_P1.3mm_Bridged12_RoundedPad1.0x1.5mm_DoubleJ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
JP7, JP10, JP13, JP16, JP19: Sample Rate; SolderJumper-2_P1.3mm_Bridged_RoundedPad1.0x1.5mm
Q2, Q3, Q4, Q5, Q6: BC807; SOT-23
R7, R12, R17, R22, R27: 12k; R_0805_2012Metric_Pad1.20x1.40mm_HandSolder
R8, R13, R18, R23, R28: 33k; R_0805_2012Metric_Pad1.20x1.40mm_HandSolder
R9, R10, R14, R15, R19, R20, R24, R25, R29, R30: 100r; R_0805_2012Metric_Pad1.20x1.40mm_HandSolder
R11, R16, R21, R26, R31: 10k; R_0805_2012Metric_Pad1.20x1.40mm_HandSolder
U2, U3, U4, U5, U6: HX711; SOP-16_4.55x10.3mm_P1.27mm

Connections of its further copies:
5VDC: C6.1, C9.1, C12.1, C15.1, C18.1, EC4.1, EC6.1, EC8.1, EC10.1, EC12.1, Q2.2 (E), Q3.2 (E), Q4.2 (E), Q5.2 (E), Q6.2 (E), R11.1, R16.1, R21.1, R26.1, R31.1, U2.1 (Vdd), U2.16 (DVdd), U3.1 (Vdd), U3.16 (DVdd), U4.1 (Vdd), U4.16 (DVdd), U5.1 (Vdd), U5.16 (DVdd), U6.1 (Vdd), U6.16 (DVdd); also elsewhere on the board
/BridgeDriver1/D_OUT: U2.12 (Dout); also elsewhere on the board
/BridgeDriver1/LC+: R10.2; also elsewhere on the board
/BridgeDriver1/LC-: R9.2; also elsewhere on the board
/BridgeDriver1/V_LC: EC3.1, JP5.2 (B), Q2.3 (C), R7.2; also elsewhere on the board
/BridgeDriver2/D_OUT: U3.12 (Dout); also elsewhere on the board
/BridgeDriver2/LC+: R15.2; also elsewhere on the board
/BridgeDriver2/LC-: R14.2; also elsewhere on the board
/BridgeDriver2/V_LC: EC5.1, JP8.2 (B), Q3.3 (C), R12.2; also elsewhere on the board
/BridgeDriver3/D_OUT: U4.12 (Dout); also elsewhere on the board
/BridgeDriver3/LC+: R20.2; also elsewhere on the board
/BridgeDriver3/LC-: R19.2; also elsewhere on the board
/BridgeDriver3/V_LC: EC7.1, JP11.2 (B), Q4.3 (C), R17.2; also elsewhere on the board
/BridgeDriver4/D_OUT: U5.12 (Dout); also elsewhere on the board
/BridgeDriver4/LC+: R25.2; also elsewhere on the board
/BridgeDriver4/LC-: R24.2; also elsewhere on the board
/BridgeDriver4/V_LC: EC9.1, JP14.2 (B), Q5.3 (C), R22.2; also elsewhere on the board
/BridgeDriver5/D_OUT: U6.12 (Dout); also elsewhere on the board
/BridgeDriver5/LC+: R30.2; also elsewhere on the board
/BridgeDriver5/LC-: R29.2; also elsewhere on the board
/BridgeDriver5/V_LC: EC11.1, JP17.2 (B), Q6.3 (C), R27.2; also elsewhere on the board
GNDA: C4.2, C6.2, C7.2, C9.2, C10.2, C12.2, C13.2, C15.2, C16.2, C18.2, EC3.2, EC4.2, EC5.2, EC6.2, EC7.2, EC8.2, EC9.2, EC10.2, EC11.2, EC12.2, JP6.2 (C), JP7.1 (A), JP9.2 (C), JP10.1 (A), JP12.2 (C), JP13.1 (A), JP15.2 (C), JP16.1 (A), JP18.2 (C), JP19.1 (A), R8.1, R13.1, R18.1, R23.1, R28.1, U2.5 (AGND), U2.14 (XI), U3.5 (AGND), U3.14 (XI), U4.5 (AGND), U4.14 (XI), U5.5 (AGND), U5.14 (XI), U6.5 (AGND), U6.14 (XI); also elsewhere on the board
unnamed: C4.1, U2.6 (VBG)
unnamed: C5.1, R9.1, U2.7 (INA-)
unnamed: C5.2, R10.1, U2.8 (INA+)
unnamed: C7.1, U3.6 (VBG)
unnamed: C8.1, R14.1, U3.7 (INA-)
unnamed: C8.2, R15.1, U3.8 (INA+)
unnamed: C10.1, U4.6 (VBG)
unnamed: C11.1, R19.1, U4.7 (INA-)
unnamed: C11.2, R20.1, U4.8 (INA+)
unnamed: C13.1, U5.6 (VBG)
unnamed: C14.1, R24.1, U5.7 (INA-)
unnamed: C14.2, R25.1, U5.8 (INA+)
unnamed: C16.1, U6.6 (VBG)
unnamed: C17.1, R29.1, U6.7 (INA-)
unnamed: C17.2, R30.1, U6.8 (INA+)
unnamed: J6.1, JP6.1 (A), U2.9 (INB-)
unnamed: J6.2, JP6.3 (B), U2.10 (INB+)
unnamed: J7.1, JP9.1 (A), U3.9 (INB-)
unnamed: J7.2, JP9.3 (B), U3.10 (INB+)
unnamed: J8.1, JP12.1 (A), U4.9 (INB-)
unnamed: J8.2, JP12.3 (B), U4.10 (INB+)
unnamed: J9.1, JP15.1 (A), U5.9 (INB-)
unnamed: J9.2, JP15.3 (B), U5.10 (INB+)
unnamed: J10.1, JP18.1 (A), U6.9 (INB-)
unnamed: J10.2, JP18.3 (B), U6.10 (INB+)
unnamed: JP5.1 (A), U2.3 (AVdd)
unnamed: JP7.2 (B), R11.2, U2.15 (Rate)
unnamed: JP8.1 (A), U3.3 (AVdd)
unnamed: JP10.2 (B), R16.2, U3.15 (Rate)
unnamed: JP11.1 (A), U4.3 (AVdd)
unnamed: JP13.2 (B), R21.2, U4.15 (Rate)
unnamed: JP14.1 (A), U5.3 (AVdd)
unnamed: JP16.2 (B), R26.2, U5.15 (Rate)
unnamed: JP17.1 (A), U6.3 (AVdd)
unnamed: JP19.2 (B), R31.2, U6.15 (Rate)
unnamed: Q2.1 (B), U2.2 (Base)
unnamed: Q3.1 (B), U3.2 (Base)
unnamed: Q4.1 (B), U4.2 (Base)
unnamed: Q5.1 (B), U5.2 (Base)
unnamed: Q6.1 (B), U6.2 (Base)
unnamed: R7.1, R8.2, U2.4 (VFB)
unnamed: R12.1, R13.2, U3.4 (VFB)
unnamed: R17.1, R18.2, U4.4 (VFB)
unnamed: R22.1, R23.2, U5.4 (VFB)
unnamed: R27.1, R28.2, U6.4 (VFB)
SCK: U2.11 (PD_SCK), U3.11 (PD_SCK), U4.11 (PD_SCK), U5.11 (PD_SCK), U6.11 (PD_SCK); also elsewhere on the board

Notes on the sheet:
CH A Jumper | Gain | Input Range -----|----|------ Open | 128 | +-20mA Short | 64 | +-40mA CH B Gain 32
Resistors: Vsup | R1 | R2 | 5v | 12k | 33k | 3.3v | 13k | 20k |
Jumper | Sample Rate -----|------- Vcc | 80Hz GND | 10Hz

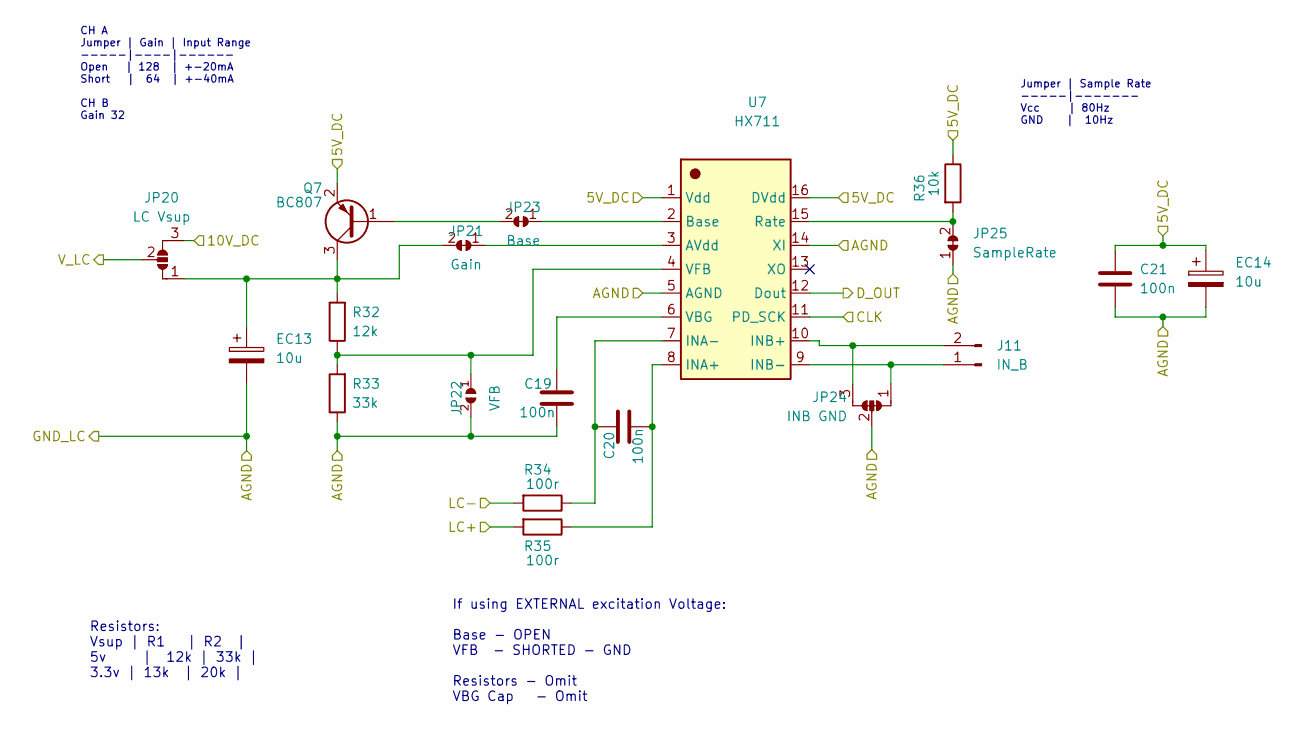
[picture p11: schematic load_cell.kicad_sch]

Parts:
C19, C20, C21: 100n; C_0805_2012Metric_Pad1.18x1.45mm_HandSolder
EC13, EC14: 10u; CP_Elec_6.3x5.9
J11: IN_B; PinHeader_1x02_P1.27mm_Vertical
JP20: LC Vsup; SolderJumper-3_P1.3mm_Open_RoundedPad1.0x1.5mm_NumberLabels
JP21: Gain; SolderJumper-2_P1.3mm_Bridged_RoundedPad1.0x1.5mm
JP22: VFB; SolderJumper-2_P1.3mm_Open_RoundedPad1.0x1.5mm
JP23: Base; SolderJumper-2_P1.3mm_Bridged_RoundedPad1.0x1.5mm
JP24: INB GND; SolderJumper-3_P1.3mm_Bridged12_RoundedPad1.0x1.5mm_DoubleJ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
JP25: SampleRate; SolderJumper-2_P1.3mm_Bridged_RoundedPad1.0x1.5mm
Q7: BC807; SOT-23
R32: 12k; R_0805_2012Metric_Pad1.20x1.40mm_HandSolder
R33: 33k; R_0805_2012Metric_Pad1.20x1.40mm_HandSolder
R34, R35: 100r; R_0805_2012Metric_Pad1.20x1.40mm_HandSolder
R36: 10k; R_0805_2012Metric_Pad1.20x1.40mm_HandSolder
U7: HX711; SOP-16_4.55x10.3mm_P1.27mm

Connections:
5VDC: C21.1, EC14.1, Q7.2 (E), R36.1, U7.1 (Vdd), U7.16 (DVdd); also elsewhere on the board
/10V_DC: JP20.3 (B); also elsewhere on the board
/LoadCell/D_OUT: U7.12 (Dout); also elsewhere on the board
/LoadCell/LC+: R35.2; also elsewhere on the board
/LoadCell/LC-: R34.2; also elsewhere on the board
/LoadCell/V_LC: JP20.2 (C); also elsewhere on the board
GNDA: C19.2, C21.2, EC13.2, EC14.2, JP22.2 (B), JP24.2 (C), JP25.1 (A), R33.1, U7.5 (AGND), U7.14 (XI); also elsewhere on the board
unnamed: C19.1, U7.6 (VBG)
unnamed: C20.1, R34.1, U7.7 (INA-)
unnamed: C20.2, R35.1, U7.8 (INA+)
unnamed: EC13.1, JP20.1 (A), JP21.2 (B), Q7.3 (C), R32.2
unnamed: J11.1, JP24.1 (A), U7.9 (INB-)
unnamed: J11.2, JP24.3 (B), U7.10 (INB+)
unnamed: JP21.1 (A), U7.3 (AVdd)
unnamed: JP22.1 (A), R32.1, R33.2, U7.4 (VFB)
unnamed: JP23.1 (A), U7.2 (Base)
unnamed: JP23.2 (B), Q7.1 (B)
unnamed: JP25.2 (B), R36.2, U7.15 (Rate)
SCK: U7.11 (PD_SCK); also elsewhere on the board

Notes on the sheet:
If using EXTERNAL excitation Voltage: Base - OPEN VFB - SHORTED - GND Resistors - Omit VBG Cap - Omit
Jumper | Sample Rate -----|------- Vcc | 80Hz GND | 10Hz
CH A Jumper | Gain | Input Range -----|----|------ Open | 128 | +-20mA Short | 64 | +-40mA CH B Gain 32
Resistors: Vsup | R1 | R2 | 5v | 12k | 33k | 3.3v | 13k | 20k |

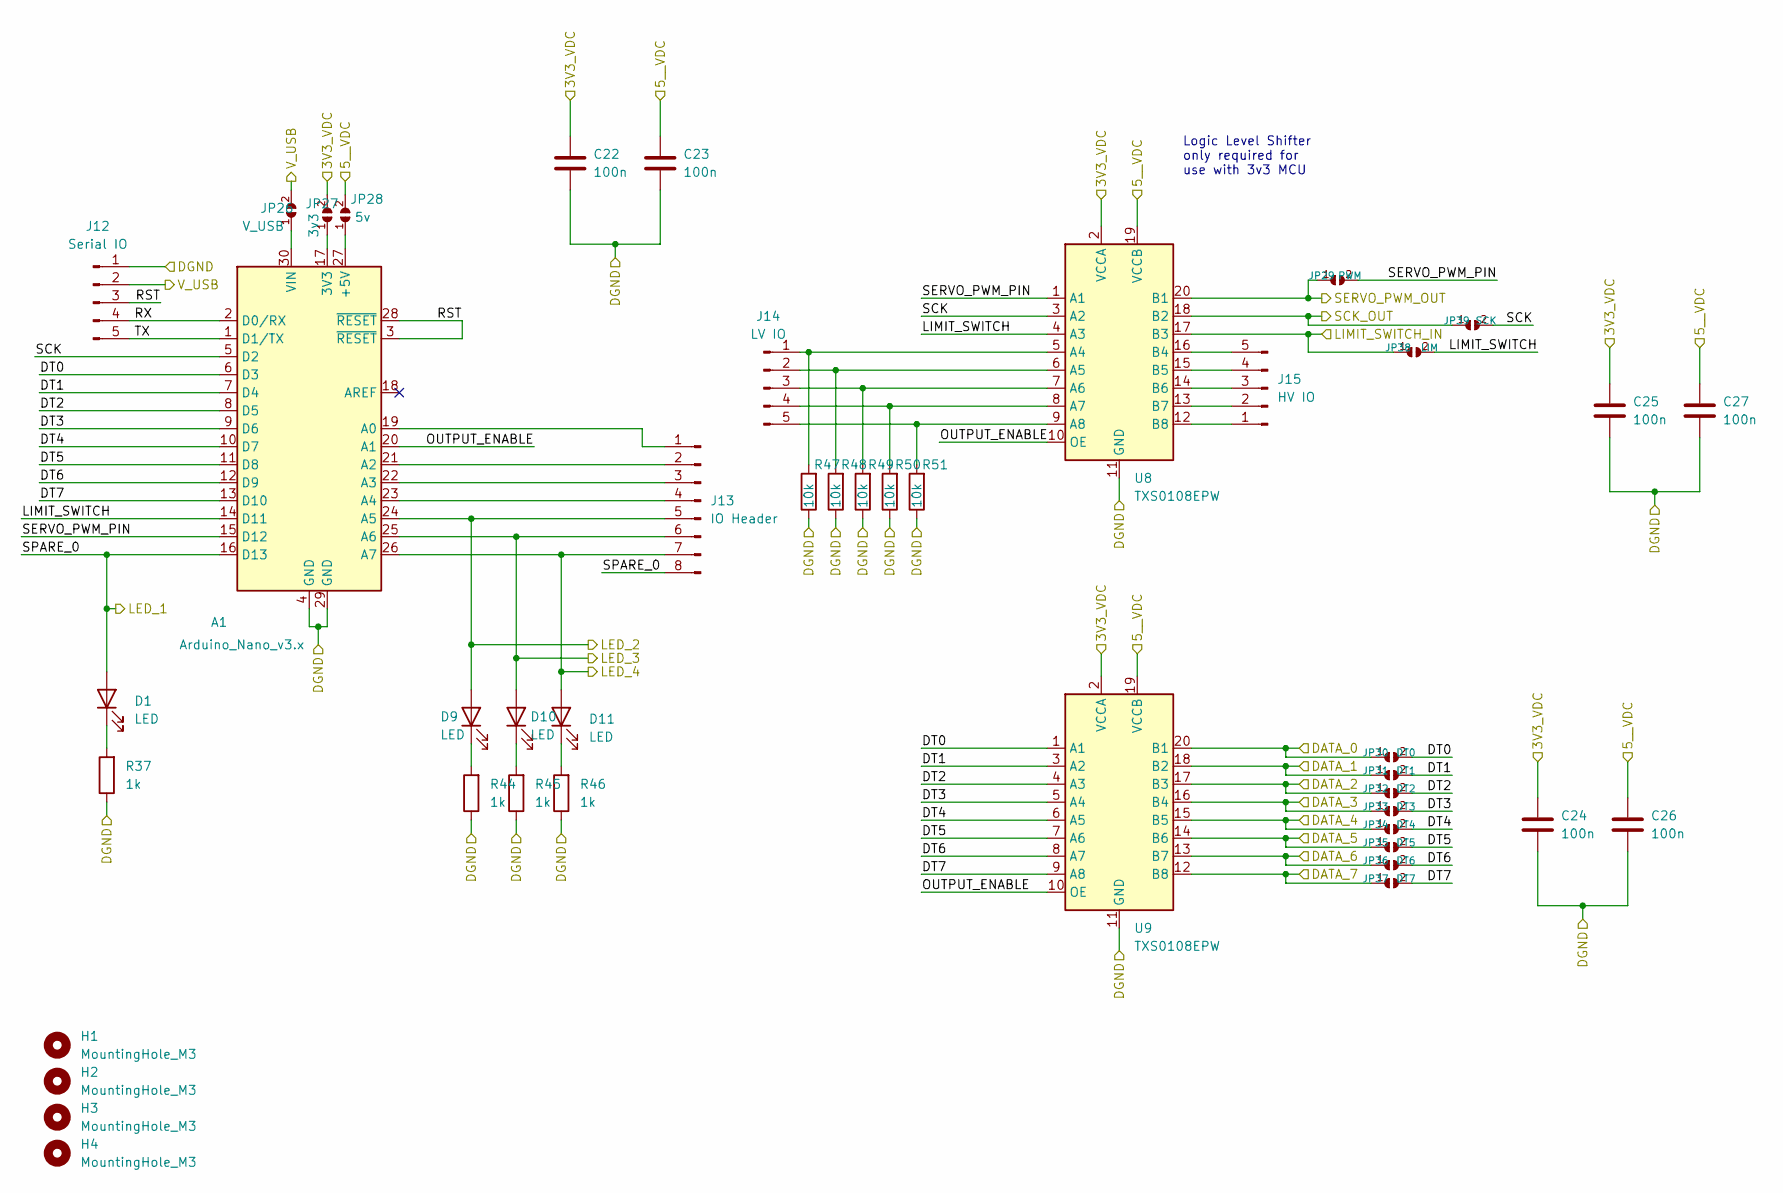
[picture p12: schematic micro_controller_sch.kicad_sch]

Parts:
A1: Arduino_Nano_v3.x; Arduino_Nano
C22, C23, C24, C25, C26, C27: 100n; C_0805_2012Metric_Pad1.18x1.45mm_HandSolder
D1, D9, D10, D11: LED; D_0805_2012Metric_Pad1.15x1.40mm_HandSolder
H1, H2, H3, H4: MountingHole_M3; MountingHole_3.2mm_M3_Pad_Via
J12: Serial IO; PinHeader_1x05_P2.54mm_Vertical
J13: IO Header; PinHeader_1x08_P2.54mm_Vertical
J14: LV IO; PinHeader_1x05_P2.54mm_Vertical
J15: HV IO; PinHeader_1x05_P2.54mm_Vertical
JP26: V_USB; SolderJumper-2_P1.3mm_Open_RoundedPad1.0x1.5mm
JP27: 3v3; SolderJumper-2_P1.3mm_Open_RoundedPad1.0x1.5mm
JP28: 5v; SolderJumper-2_P1.3mm_Open_RoundedPad1.0x1.5mm
JP29: PWM; SolderJumper-2_P1.3mm_Open_RoundedPad1.0x1.5mm
JP30: DT0; SolderJumper-2_P1.3mm_Open_RoundedPad1.0x1.5mm
JP31: DT1; SolderJumper-2_P1.3mm_Open_RoundedPad1.0x1.5mm
JP32: DT2; SolderJumper-2_P1.3mm_Open_RoundedPad1.0x1.5mm
JP33: DT3; SolderJumper-2_P1.3mm_Open_RoundedPad1.0x1.5mm
JP34: DT4; SolderJumper-2_P1.3mm_Open_RoundedPad1.0x1.5mm
JP35: DT5; SolderJumper-2_P1.3mm_Open_RoundedPad1.0x1.5mm
JP36: DT6; SolderJumper-2_P1.3mm_Open_RoundedPad1.0x1.5mm
JP37: DT7; SolderJumper-2_P1.3mm_Open_RoundedPad1.0x1.5mm
JP38: LIM; SolderJumper-2_P1.3mm_Open_RoundedPad1.0x1.5mm
JP39: SCK; SolderJumper-2_P1.3mm_Open_RoundedPad1.0x1.5mm
R37, R44, R45, R46: 1k; R_0805_2012Metric_Pad1.20x1.40mm_HandSolder
R47, R48, R49, R50, R51: 10k; R_0805_2012Metric_Pad1.20x1.40mm_HandSolder
U8, U9: TXS0108EPW; TSSOP-20_4.4x6.5mm_P0.65mm

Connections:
3V3DC: C22.1, C24.1, C25.1, JP27.2 (B), U8.2 (VCCA), U9.2 (VCCA); also elsewhere on the board
5VDC: C23.1, C26.1, C27.1, JP28.2 (B), U8.19 (VCCB), U9.19 (VCCB); also elsewhere on the board
/BridgeDriver0/D_OUT: JP30.1 (A), U9.20 (B1); also elsewhere on the board
/BridgeDriver1/D_OUT: JP31.1 (A), U9.18 (B2); also elsewhere on the board
/BridgeDriver2/D_OUT: JP32.1 (A), U9.17 (B3); also elsewhere on the board
/BridgeDriver3/D_OUT: JP33.1 (A), U9.16 (B4); also elsewhere on the board
/BridgeDriver4/D_OUT: JP34.1 (A), U9.15 (B5); also elsewhere on the board
/BridgeDriver5/D_OUT: JP35.1 (A), U9.14 (B6); also elsewhere on the board
/LIMIT_SWITCH: JP38.1 (A), U8.17 (B3); also elsewhere on the board
/LoadCell/D_OUT: JP36.1 (A), U9.13 (B7); also elsewhere on the board
/MCU/DATA_7: JP37.1 (A), U9.12 (B8)
/MCU/DT0: A1.6 (D3), JP30.2 (B), U9.1 (A1)
/MCU/DT1: A1.7 (D4), JP31.2 (B), U9.3 (A2)
/MCU/DT2: A1.8 (D5), JP32.2 (B), U9.4 (A3)
/MCU/DT3: A1.9 (D6), JP33.2 (B), U9.5 (A4)
/MCU/DT4: A1.10 (D7), JP34.2 (B), U9.6 (A5)
/MCU/DT5: A1.11 (D8), JP35.2 (B), U9.7 (A6)
/MCU/DT6: A1.12 (D9), JP36.2 (B), U9.8 (A7)
/MCU/DT7: A1.13 (D10), JP37.2 (B), U9.9 (A8)
/MCU/LED_2: A1.24 (A5), D9.2 (A), J13.5; also elsewhere on the board
/MCU/LED_3: A1.25 (A6), D10.2 (A), J13.6; also elsewhere on the board
/MCU/LED_4: A1.26 (A7), D11.2 (A), J13.7; also elsewhere on the board
/MCU/LIMIT_SWITCH: A1.14 (D11), JP38.2 (B), U8.4 (A3)
/MCU/OUTPUT_ENABLE: A1.20 (A1), U8.10 (OE), U9.10 (OE)
/MCU/RST: A1.3 (~RESET), A1.28 (~RESET), J12.3
/MCU/RX: A1.2 (D0/RX), J12.4
/MCU/SCK: A1.5 (D2), JP39.2 (B), U8.3 (A2)
/MCU/SERVO_PWM_PIN: A1.15 (D12), JP29.2 (B), U8.1 (A1)
/MCU/SPARE_0: A1.16 (D13), D1.2 (A), J13.8; also elsewhere on the board
/MCU/TX: A1.1 (D1/TX), J12.5
/MCU/V_USB: J12.2, JP26.2 (B)
/SERVO_PWM: JP29.1 (A), U8.20 (B1); also elsewhere on the board
GNDA: A1.4 (GND), A1.29 (GND), C22.2, C23.2, C24.2, C25.2, C26.2, C27.2, J12.1, R37.1, R44.1, R45.1, R46.1, R47.1, R48.1, R49.1, R50.1, R51.1, U8.11 (GND), U9.11 (GND); also elsewhere on the board
unnamed: A1.17 (3V3), JP27.1 (A)
unnamed: A1.19 (A0), J13.1
unnamed: A1.21 (A2), J13.2
unnamed: A1.22 (A3), J13.3
unnamed: A1.23 (A4), J13.4
unnamed: A1.27 (+5V), JP28.1 (A)
unnamed: A1.30 (VIN), JP26.1 (A)
unnamed: D1.1 (K), R37.2
unnamed: D9.1 (K), R44.2
unnamed: D10.1 (K), R45.2
unnamed: D11.1 (K), R46.2
unnamed: J14.1, R47.2, U8.5 (A4)
unnamed: J14.2, R48.2, U8.6 (A5)
unnamed: J14.3, R49.2, U8.7 (A6)
unnamed: J14.4, R50.2, U8.8 (A7)
unnamed: J14.5, R51.2, U8.9 (A8)
unnamed: J15.1, U8.12 (B8)
unnamed: J15.2, U8.13 (B7)
unnamed: J15.3, U8.14 (B6)
unnamed: J15.4, U8.15 (B5)
unnamed: J15.5, U8.16 (B4)
SCK: JP39.1 (A), U8.18 (B2); also elsewhere on the board

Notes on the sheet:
Logic Level Shifter only required for use with 3v3 MCU

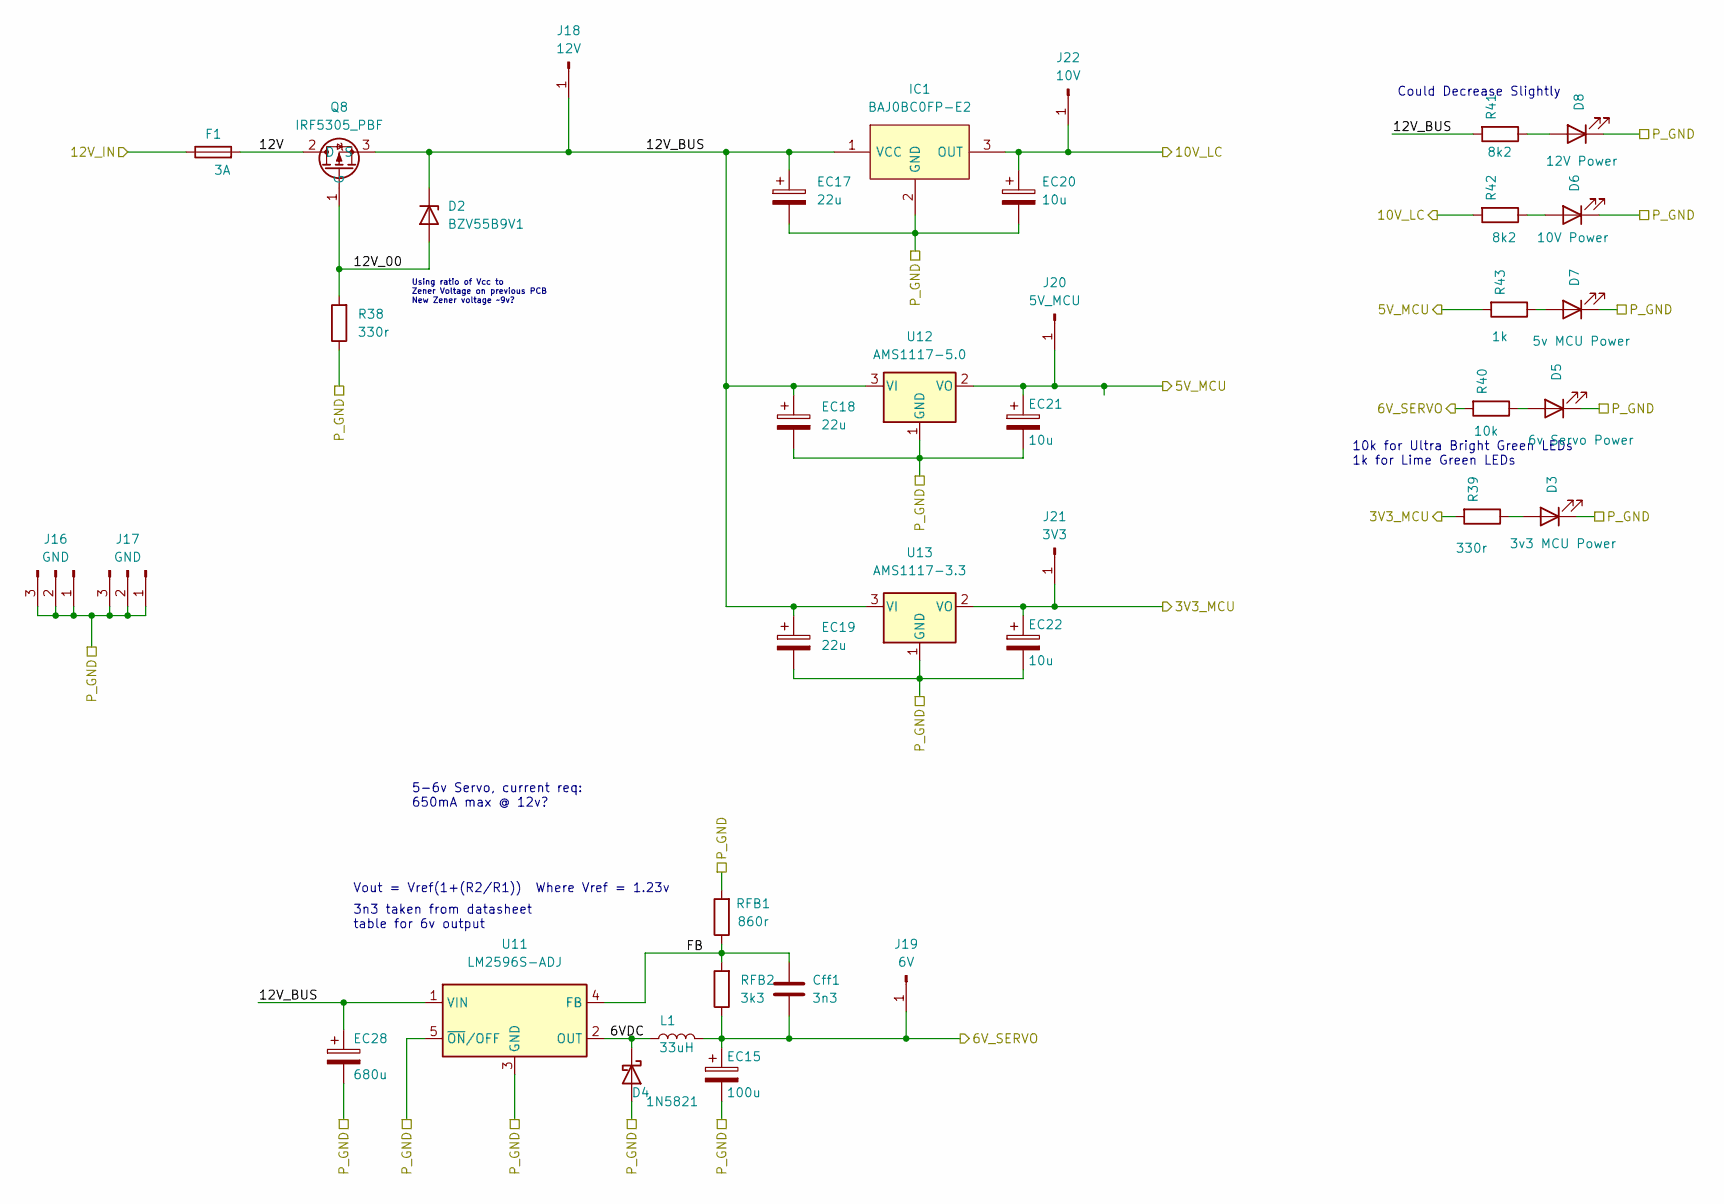
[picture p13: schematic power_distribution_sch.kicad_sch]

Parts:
Cff1: 3n3; C_0805_2012Metric_Pad1.18x1.45mm_HandSolder
D2: BZV55B9V1; D_MiniMELF
D3: 3v3 MCU Power; D_0805_2012Metric_Pad1.15x1.40mm_HandSolder
D4: 1N5821; D_SMA
D5: 6v Servo Power; D_0805_2012Metric_Pad1.15x1.40mm_HandSolder
D6: 10V Power; D_0805_2012Metric_Pad1.15x1.40mm_HandSolder
D7: 5v MCU Power; D_0805_2012Metric_Pad1.15x1.40mm_HandSolder
D8: 12V Power; D_0805_2012Metric_Pad1.15x1.40mm_HandSolder
EC15: 100u; CP_Elec_10x10
EC17, EC18, EC19: 22u; CP_Elec_6.3x5.9
EC20, EC21, EC22: 10u; CP_Elec_6.3x5.9
EC28: 680u; CP_Elec_10x10
F1: 3A; Fuseholder_Cylinder-5x20mm_Stelvio-Kontek_PTF78_Horizontal_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
IC1: BAJ0BC0FP-E2; TO-252-2; Manufacturer_Part_Number BAJ0BC0FP-E2
J16, J17: GND; PinHeader_1x03_P2.54mm_Vertical
J18: 12V; PinHeader_1x01_P2.54mm_Vertical
J19: 6V; PinHeader_1x01_P2.54mm_Vertical
J20: 5V_MCU; PinHeader_1x01_P2.54mm_Vertical
J21: 3V3; PinHeader_1x01_P2.54mm_Vertical
J22: 10V; PinHeader_1x01_P2.54mm_Vertical
L1: 33uH; L_12x12mm_H8mm
Q8: IRF5305_PBF; TO-220-3_Vertical
R38, R39: 330r; R_0805_2012Metric_Pad1.20x1.40mm_HandSolder
R40: 10k; R_0805_2012Metric_Pad1.20x1.40mm_HandSolder
R41, R42: 8k2; R_0805_2012Metric_Pad1.20x1.40mm_HandSolder
R43: 1k; R_0805_2012Metric_Pad1.20x1.40mm_HandSolder
RFB1: 860r; R_0805_2012Metric_Pad1.20x1.40mm_HandSolder
RFB2: 3k3; R_0805_2012Metric_Pad1.20x1.40mm_HandSolder
U11: LM2596S-ADJ; TO-263-5_TabPin3
U12: AMS1117-5.0; SOT-223-3_TabPin2
U13: AMS1117-3.3; SOT-223-3_TabPin2

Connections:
3V3DC: EC22.1, J21.1, R39.2, U13.2 (VO); also elsewhere on the board
5VDC: EC21.1, J20.1, R43.2, U12.2 (VO); also elsewhere on the board
/10V_DC: EC20.1, IC1.3 (OUT), J22.1, R42.2; also elsewhere on the board
/Power Distribution/6VDC: D4.1 (K), L1.1, U11.2 (OUT)
/Power Distribution/12V: F1.2, Q8.2 (D)
/Power Distribution/12V_00: D2.2 (A), Q8.1 (G), R38.2
/Power Distribution/12V_BUS: D2.1 (K), EC17.1, EC18.1, EC19.1, EC28.1, IC1.1 (VCC), J18.1, Q8.3 (S), R41.2, U11.1 (VIN), U12.3 (VI), U13.3 (VI)
/Power Distribution/12V_IN: F1.1; also elsewhere on the board
/Power Distribution/FB: Cff1.1, RFB1.1, RFB2.2, U11.4 (FB)
/SERVO_POWER: Cff1.2, EC15.1, J19.1, L1.2, R40.2, RFB2.1; also elsewhere on the board
GNDPWR: D3.1 (K), D4.2 (A), D5.1 (K), D6.1 (K), D7.1 (K), D8.1 (K), EC15.2, EC17.2, EC18.2, EC19.2, EC20.2, EC21.2, EC22.2, EC28.2, IC1.2 (GND), J16.1, J16.2, J16.3, J17.1, J17.2, J17.3, R38.1, RFB1.2, U11.3 (GND), U11.5 (~ON/OFF), U12.1 (GND), U13.1 (GND); also elsewhere on the board
unnamed: D3.2 (A), R39.1
unnamed: D5.2 (A), R40.1
unnamed: D6.2 (A), R42.1
unnamed: D7.2 (A), R43.1
unnamed: D8.2 (A), R41.1

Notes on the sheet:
3n3 taken from datasheet table for 6v output
10k for Ultra Bright Green LEDs 1k for Lime Green LEDs
5-6v Servo, current req: 650mA max @ 12v?
Could Decrease Slightly
Using ratio of Vcc to Zener Voltage on previous PCB New Zener voltage ~9v?
Vout = Vref(1+(R2/R1)) Where Vref = 1.23v

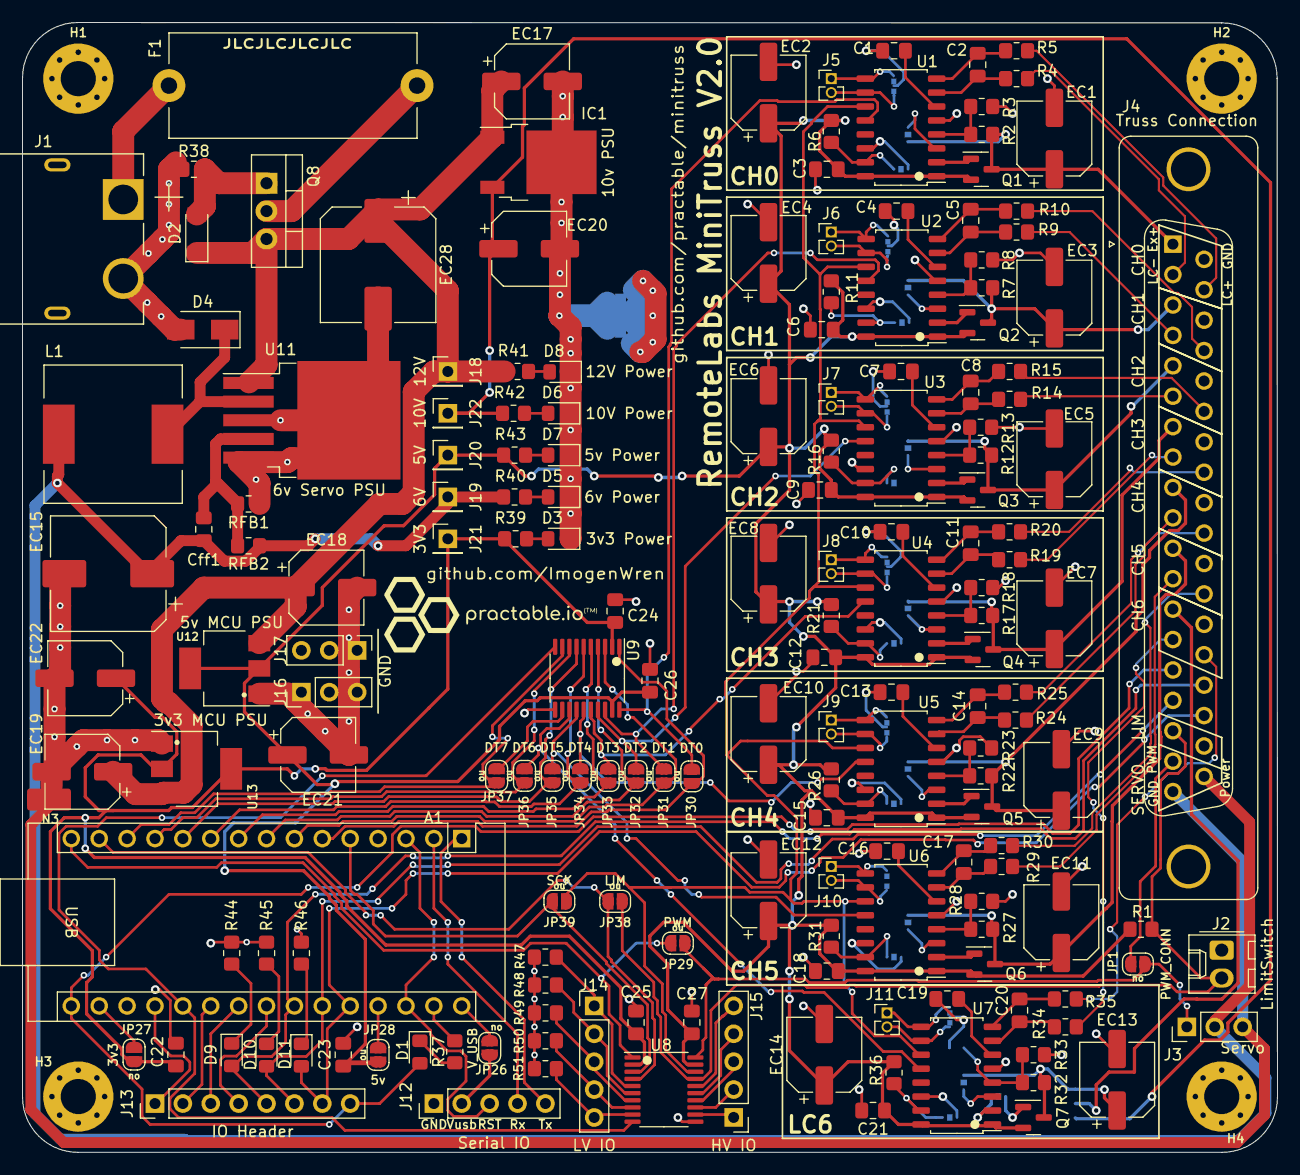
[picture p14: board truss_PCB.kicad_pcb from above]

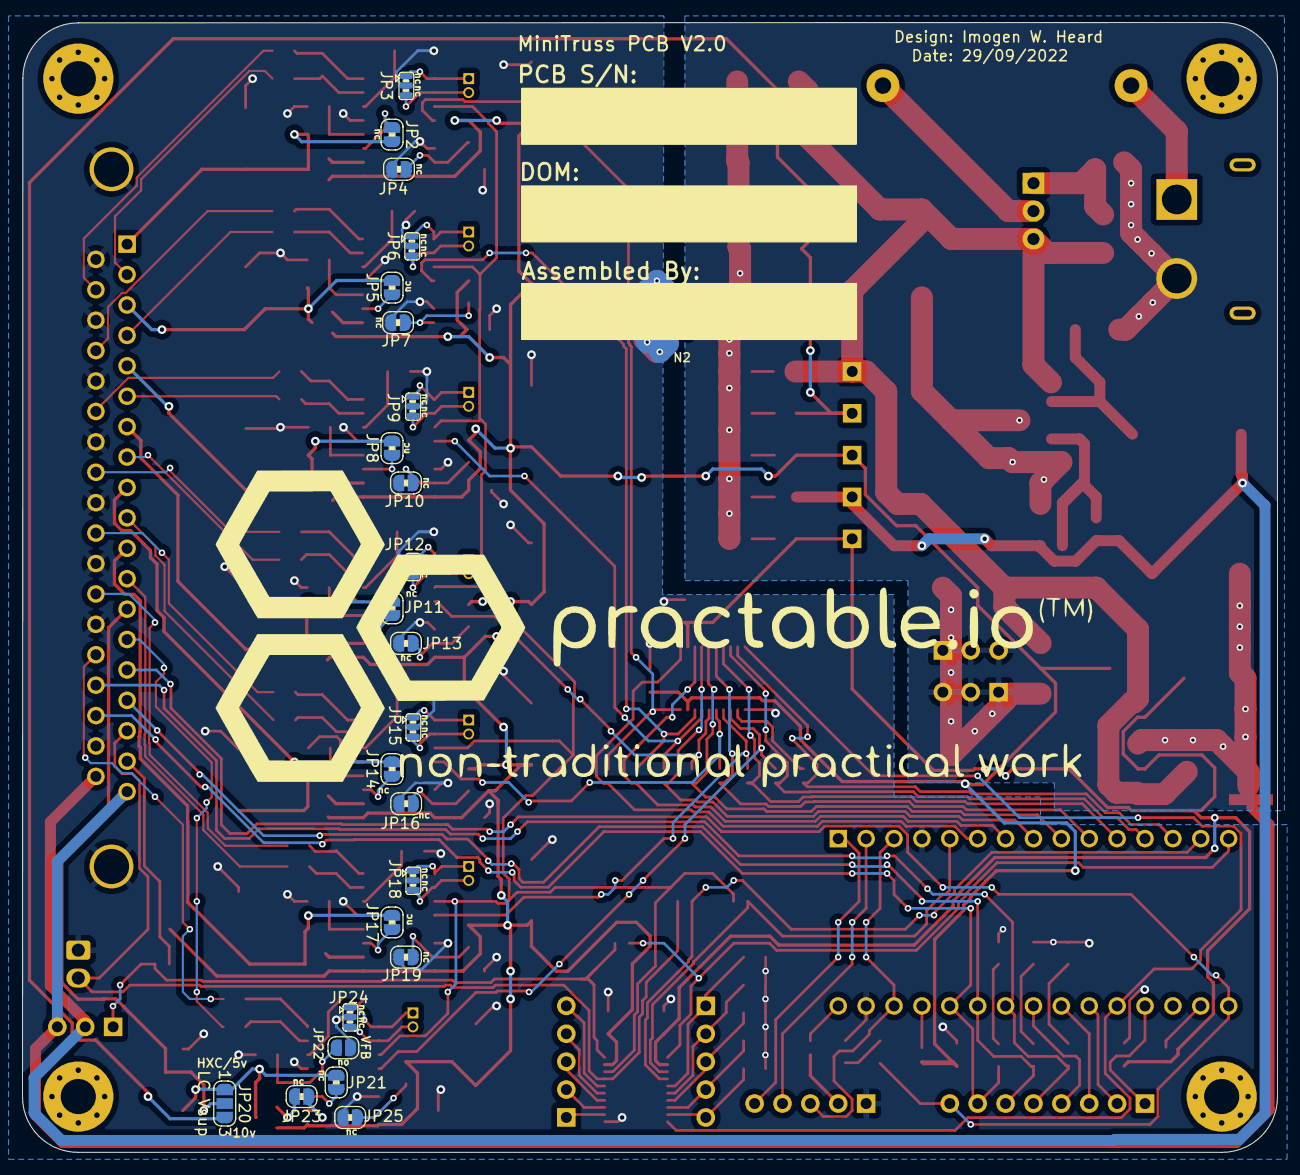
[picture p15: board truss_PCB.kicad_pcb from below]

Board: 2 copper layers, 114.3 x 102.9 mm, 205 parts (25 on the bottom side), 157 nets.

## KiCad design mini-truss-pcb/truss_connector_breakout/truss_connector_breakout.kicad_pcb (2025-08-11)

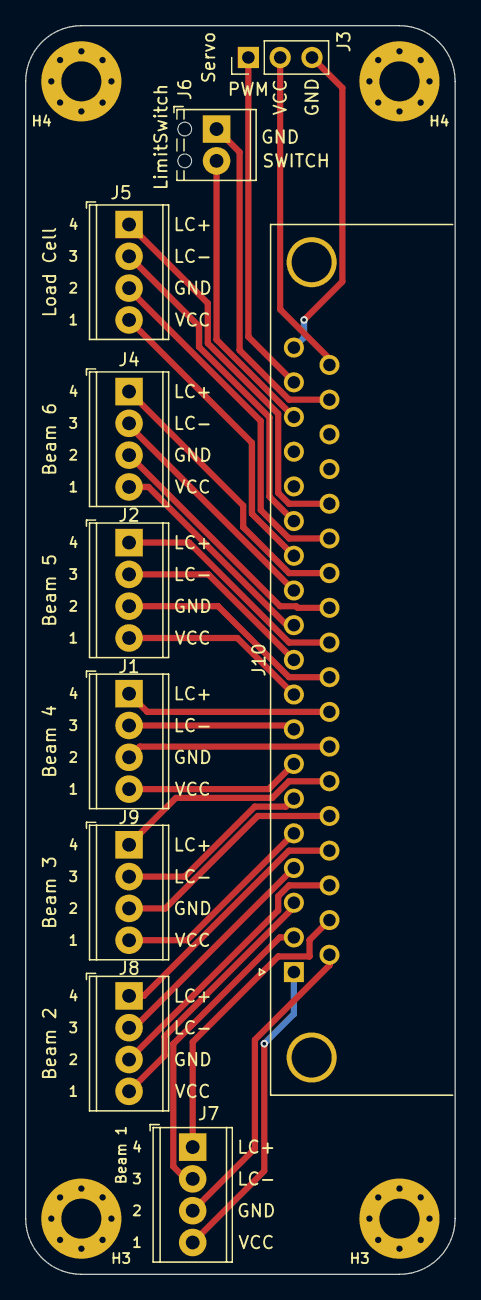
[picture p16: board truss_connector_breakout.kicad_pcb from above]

Board: 2 copper layers, 34.3 x 99.7 mm, 14 parts (0 on the bottom side), 33 nets.

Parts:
H3, H3#2, H4, H4#2: MountingHole_M3; MountingHole_3.2mm_M3_Pad_Via
J1: D3; TerminalBlock_Phoenix_MPT-0,5-4-2.54_1x04_P2.54mm_Horizontal
J2: D4; TerminalBlock_Phoenix_MPT-0,5-4-2.54_1x04_P2.54mm_Horizontal
J3: Servo; PinHeader_1x03_P2.54mm_Vertical
J4: D5; TerminalBlock_Phoenix_MPT-0,5-4-2.54_1x04_P2.54mm_Horizontal
J5: D6; TerminalBlock_Phoenix_MPT-0,5-4-2.54_1x04_P2.54mm_Horizontal
J6: LimitSwitch; TerminalBlock_Phoenix_MPT-0,5-2-2.54_1x02_P2.54mm_Horizontal
J7: D0; TerminalBlock_Phoenix_MPT-0,5-4-2.54_1x04_P2.54mm_Horizontal
J8: D1; TerminalBlock_Phoenix_MPT-0,5-4-2.54_1x04_P2.54mm_Horizontal
J9: D2; TerminalBlock_Phoenix_MPT-0,5-4-2.54_1x04_P2.54mm_Horizontal
J10: Truss Connector; DSUB-37_Male_Horizontal_P2.77x2.84mm_EdgePinOffset9.90mm_Ho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

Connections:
/D0_GND: J7.3, J10.20
/D0_LC+: J7.1, J10.21
/D0_LC-: J7.2, J10.2
/D0_VCC: J7.4, J10.1
/D1_GND: J8.3, J10.22
/D1_LC+: J8.1, J10.23
/D1_LC-: J8.2, J10.4
/D1_VCC: J8.4, J10.3
/D2_GND: J9.3, J10.24
/D2_LC+: J9.1, J10.25
/D2_LC-: J9.2, J10.6
/D2_VCC: J9.4, J10.5
/D3_GND: J1.3, J10.26
/D3_LC+: J1.1, J10.27
/D3_LC-: J1.2, J10.8
/D3_VCC: J1.4, J10.7
/D4_GND: J2.3, J10.28
/D4_LC+: J2.1, J10.29
/D4_LC-: J2.2, J10.10
/D4_VCC: J2.4, J10.9
/D5_GND: J4.3, J10.30
/D5_LC+: J4.1, J10.31
/D5_LC-: J4.2, J10.12
/D5_VCC: J4.4, J10.11
/D6_GND: J5.3, J10.32
/D6_LC+: J5.1, J10.33
/D6_LC-: J5.2, J10.14
/D6_VCC: J5.4, J10.13
/LIMIT_SWITCH: J6.2, J10.17
/LS_GND: J6.1, J10.36
/PWM_SERVO: J3.1, J10.18
/SERVO_GND: J3.3, J10.19
/SERVO_VCC: J3.2, J10.37

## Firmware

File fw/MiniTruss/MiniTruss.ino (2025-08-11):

  "servo",
  "home",
  "docal",
  "sample",
  "print",
  "stream",
  "endst",
  "secret",
  "gtscrt"
  "savcal",
  "getcal",
  "info",





//Firmware for MiniTruss remote lab experiment
// Single controller firmware with state machine for reading and writing.

//Author: David P. Reid
//dprydereid@gmail.com
// 17/03/22

// Update for new LinearServo load control
// 02/05/22
// dprydereid@gmail.com

// Added new WAIT state and READ state now only measures 1 gauge every loop of the state so as not to remain in read state for too long, reducing responsiveness.
// 08/06/22
// dprydereid@gmail.com

// Add a hardware limit switch state and updated load cell pin
// 01/09/22
// dprydereid@gmail.com

// Updated with secure flash storage of calibration data using https://github.com/timdrysdale/nanoflash 
//14/09/22

// Because of slightly different behaviour on different truss setups, have updated the resetting of the truss so that it performs a reset here on startup, but that
//"zeroing" on the UI is really just setting to zero position rather than performing the reset function - which is only really to be used for a hard reset on power
// loss.

// 06/10/22 Added the ability to place hardware back in original startup state -> allows updating of calibration data without power cycle.
// 07/10/22 Increased the number of writes possible (from 3 to 10) to flash storage before requiring reloading firmware

// IMPORT LIBRARIES
#include "HX711.h"
#include "LinearServo.h"
#include "ArduinoJson-v6.9.1.h"
#include <FlashStorage.h>

//JSON serialization
#define COMMAND_SIZE 192  //originally 64 - increased for length of cal data + uuid authorization https://arduinojson.org/v6/assistant
StaticJsonDocument<COMMAND_SIZE> doc;
char command[COMMAND_SIZE];

//Linear actuator VARIABLES
#define DRIVE 12
//#define SDIR 15
//#define SPUL 16

int currentPos = 0;     //the position of the servo as output from LinearServo library
int moveToPos = 0;      //the position the servo should move to between 0 (full retraction) to 100 (full extension)
int max_position = 20;  //% extension of linear actuator
LinearServo servo = LinearServo(DRIVE, max_position);

unsigned long move_interval = 5000L;    //this is updated depending on the move distance
unsigned long step_interval = 100L;     //at 5V takes approx. 100ms to move 1 position
unsigned long enter_move_time = millis();    //the time at which the move state started

//LIMIT SWITCHES
#define limitSwitch 11
volatile bool limitReached = false;
unsigned long lastDebounceTime = 0;  // the last time the interrupt was triggered
unsigned long debounceDelay = 50000;    // micro-seconds the debounce time; 
int soft_limit = 15;        //need to have a soft limit which the servo returns to if it hits the hard limit switch

//GAUGE READINGS
const int numGauges = 7;    //6 gauges + load cell
float data[numGauges] = {0.0, 0.0, 0.0, 0.0, 0.0, 0.0, 0.0};


//GAUGE SETUP
const int SCK_PIN = 2;  //Common CLOCK pin
const int GAUGE_0_DT = 9; //DATA pins, //LOAD CELL
const int GAUGE_1_DT = 3; //TRUSS MEMBER 1
const int GAUGE_2_DT = 4; //TRUSS MEMBER 2
const int GAUGE_3_DT = 5; //TRUSS MEMBER 3
const int GAUGE_4_DT = 6; //TRUSS MEMBER 4
const int GAUGE_5_DT = 7; //TRUSS MEMBER 5
const int GAUGE_6_DT = 8; //TRUSS MEMBER 6 

int read_index = 0;   //holds a flag for which gauge to read on next loop of state machine.

const int pins[numGauges] = {GAUGE_0_DT, GAUGE_1_DT, GAUGE_2_DT, GAUGE_3_DT, GAUGE_4_DT, GAUGE_5_DT, GAUGE_6_DT};

HX711 gauge_0;
HX711 gauge_1;
HX711 gauge_2;
HX711 gauge_3;
HX711 gauge_4;
HX711 gauge_5;
HX711 gauge_6;

//these will need to be calibrated for new truss setup
// OLD values for large truss
//const float scale_load = -15184;
//const float scale_factor_1 = 4050;
//const float scale_factor_2 = scale_factor_1*1.030;
//const float scale_factor_3 = scale_factor_1*0.977;
//const float scale_factor_4 = scale_factor_1*0.947;
//const float scale_factor_5 = scale_factor_1*0.818;
//const float scale_factor_6 = scale_factor_1*0.924;

//these are the average values of the first 8 trusses. The specific calibration data for each truss is loaded at startup.
float scale_load = -371.8;
float scale_factor_1 = 69.84;
float scale_factor_2 = 99.27;
float scale_factor_3 = 34.44;
float scale_factor_4 = 178.82;
float scale_factor_5 = 67.30;
float scale_factor_6 = 47.86;


HX711 gauges[numGauges] = {gauge_0, gauge_1, gauge_2, gauge_3, gauge_4, gauge_5, gauge_6};


//TIMING FOR GAUGE WRITING
unsigned long timeInterval = 1000;    //write out gauge readings with a period no smaller than 1s
unsigned long previousTime = 0;

//TIMING FOR WAIT STATE
unsigned long waitInterval = 2000;    //this changes depending on what is being waited for.
unsigned long waitStartTime = 0;

//Additional variables for new Truss PCB design - Imogen Heard 18/08/22
#define OUTPUT_ENABLE A1   // Must be set high if using Logic Level Shifters

// SECURE CALIBRATION VARIABLES ============================

#define FLASH_WRITES_MAX 10
#define SECRET_LEN_MAX 99
#define SCALE_FACTOR_LEN 7

// calibration value indices in cal array
#define LOAD_CELL 0
#define MEMBER_1 1
#define MEMBER_2 2
#define MEMBER_3 3
#define MEMBER_4 4
#define MEMBER_5 5
#define MEMBER_6 6

// Create a structure that stores the cal data
typedef struct {
  boolean secure;          // Set this true when secret is first written 
  boolean valid;           // Set this true when calibration data is first written
  char secret[SECRET_LEN_MAX];  // Secret string for authorising calibration updates (typically a uuid of 36 chars in form 8-4-4-4-12)
  int  writes;             // Count number of remaining writes we'll permit
  // You can change the values below here to suit your experiment
  float scale_factor[SCALE_FACTOR_LEN];   // Scale factors for some experiment or other
} Calibration;

// Create a global "Calibration" variable and call it cal
Calibration cal;

// Reserve a portion of flash memory to store a "Calibration" and
// call it "cal_store".
FlashStorage(cal_store, Calibration);

/**
 * Defines the valid states for the state machine
 * 
 */
typedef enum
{
  STATE_STANDBY = 0,        //no drive to motor, no reading of gauges
  STATE_READ = 1,           //reads each gauge
  STATE_MOVE = 2,           //allows stepper motor to move to new position
  STATE_ZERO = 3,           //zeroes the position of the servo
  STATE_TARE_GAUGES = 4,           //tares (zeroes) the gauge readings
  STATE_TARE_LOAD = 5,      //tares the load force gauge
  STATE_TARE_ALL = 6,      //tares both the gauges and load cell
  STATE_GAUGE_RESET = 7,    //resets all gauges
  STATE_WAIT = 8,    //a wait state to allow functions like taring to complete before returning to READ state.
  STATE_CALIBRATE = 9,
  STATE_STARTUP = 10,        // anything to do with starting up the experiment
  STATE_SETSECRET = 11,     // await authorisation setup before accepting calibration data
  STATE_SETCAL = 12,       // await a calibration data before beginning normal operation of the experiment
  STATE_LOADCAL = 13,      // update calibration
  
} StateType;

//state Machine function prototypes
//these are the functions that run whilst in each respective state.
void Sm_State_Standby(void);
void Sm_State_Read(void);
void Sm_State_Move(void);
void Sm_State_Zero(void);
void Sm_State_Tare_Gauges(void);
void Sm_State_Tare_Load(void);
void Sm_State_Tare_All(void);
void Sm_State_Gauge_Reset(void);
void Sm_State_Wait(void);
void Sm_State_Calibrate(void);
void Sm_State_StartUp(void);
void Sm_State_SetSecret(void);
void Sm_State_SetCal(void);
void Sm_State_LoadCal(void);

// cal function prototypes (here because readSerialJSON has to come after StateType definition)
bool cal_is_secure();
bool cal_is_valid();
void startTimer(int);
void report_cal();
void cal_set_secret(const char *);
void cal_set_values(StaticJsonDocument<COMMAND_SIZE>);
StateType readSerialJSON(StateType); //has to come after type definition

/**
 * Type definition used to define the state
 */
 
typedef struct
{
  StateType State; /**< Defines the command */
  void (*func)(void); /**< Defines the function to run */
} StateMachineType;

/**
 * A table that defines the valid states of the state machine and
 * the function that should be executed for each state
 */
StateMachineType StateMachine[] =
{
  {STATE_STANDBY, Sm_State_Standby},
  {STATE_READ, Sm_State_Read},
  {STATE_MOVE, Sm_State_Move},
  {STATE_ZERO, Sm_State_Zero},
  {STATE_TARE_GAUGES, Sm_State_Tare_Gauges},
  {STATE_TARE_LOAD, Sm_State_Tare_Load},
  {STATE_TARE_ALL, Sm_State_Tare_All},
  {STATE_GAUGE_RESET, Sm_State_Gauge_Reset},
  {STATE_WAIT, Sm_State_Wait},
  {STATE_CALIBRATE, Sm_State_Calibrate},
  {STATE_STARTUP,     Sm_State_StartUp},
  {STATE_SETSECRET,   Sm_State_SetSecret}, 
  {STATE_SETCAL,      Sm_State_SetCal},
  {STATE_LOADCAL,     Sm_State_LoadCal}, 

};
 
int NUM_STATES = 14;

/**
 * Stores the current state of the state machine
 */
 
StateType SmState = STATE_STARTUP;    //STATE_GAUGE_RESET will need to be reached before correct functioning

//TESTING ONLY
//unsigned long reportInterval = 1000;    //write out cal data
//unsigned long previousReport = 0;


//DEFINE STATE MACHINE FUNCTIONS================================================================

//TRANSITION: STATE_STANDBY -> STATE_STANDBY
void Sm_State_Standby(void){

//TESTING
//  if(millis() - previousReport >= reportInterval){
//    report_cal_loaded();
//    previousReport = millis();
//  }
  
  SmState = STATE_STANDBY;
  
}

//+++++++++++++++++++++++++++++++++++++++++++++++++++++++++++++++++++++++ READ ++++++++++++++++++++++++++++++++++++++++++++++++++++++++++++
//TRANSITION: STATE_READ -> STATE_READ
// State Read reads the next gauge and stores the data for reporting.
// Remains in read state until user makes the change.
void Sm_State_Read(void){

  if(millis() - previousTime >= timeInterval){
  
   //for(int i=0; i< numGauges; i++){
      //if(gaugeScales[i].wait_ready_timeout(100)){
      if(gauges[read_index].is_ready()){
        
        data[read_index] = gauges[read_index].get_units(10);       //what is the best number of readings to take?
        
      } 

      //delay(10);    //necessary?
   //}

    read_index = (read_index + 1) % numGauges;    //move to next read_index and loop back to 0 after numGauges reached
    report();
    previousTime = millis();
    
  }
  
   SmState = STATE_READ;
  
}


//+++++++++++++++++++++++++++++++++++++++++++++++++++++++++++++++++++++++ MOVE ++++++++++++++++++++++++++++++++++++++++++++++++++++++++++++
//TRANSITION: STATE_MOVE -> STATE_READ
//Remains in move state for an appropriate time to complete the move. There is no feedback on position from servo so need to base on time.
//This blocks gauge reading, but high servo speed and slow update of gauges should make this fine.
void Sm_State_Move(void){

  // can only run servo in move state if the lower limit has not been activated
  if(!limitReached)
  {
    currentPos = servo.update();
   
   if(millis() - enter_move_time >= move_interval){
    
      SmState = STATE_READ;
    
   } 
   else
   {
    
      SmState = STATE_MOVE;
    
   }
  } 
  else 
  {
    
    SmState = STATE_READ;
    
  }
  
}

//+++++++++++++++++++++++++++++++++++++++++++++++++++++++++++++++++++++++ ZERO ++++++++++++++++++++++++++++++++++++++++++++++++++++++++++++
//TRANSITION: STATE_ZERO -> STATE_READ
//
void Sm_State_Zero(void){
  
  servo.zero();

  currentPos = 0;
  
  waitStartTime = millis();
  waitInterval = 3000;

  limitReached = false;
  SmState = STATE_WAIT;
 
}

//+++++++++++++++++++++++++++++++++++++++++++++++++++++++++++++++++++++++ TARE GAUGES++++++++++++++++++++++++++++++++++++++++++++++++++++++++++++
//TRANSITION: STATE_TARE_GAUGES -> STATE_WAIT
void Sm_State_Tare_Gauges(void){
  
  tareGauges();

  waitStartTime = millis();
  waitInterval = 2000;

  SmState = STATE_WAIT;
  
}
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

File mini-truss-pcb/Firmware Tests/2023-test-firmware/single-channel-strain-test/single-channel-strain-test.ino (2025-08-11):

#include <Arduino.h>
#include "HX711.h"
#include <buttonObject.h>  // Does not work with the HX711 libary! :(
#include <autoDelay.h>
#include <ledObject.h>

/*

How to calibrate your load cell
Call set_scale() with no parameter.
Call tare() with no parameter.
Place a known weight on the scale and call get_units(10).
Divide the result in step 3 to your known weight. You should get about the parameter you need to pass to set_scale().
Adjust the parameter in step 4 until you get an accurate reading.


*/

// HX711 circuit wiring
const int LOADCELL_DO0_PIN = 3;
const int LOADCELL_DO1_PIN = 4;
const int LOADCELL_DO2_PIN = 5;
const int LOADCELL_DO3_PIN = 6;
const int LOADCELL_DO4_PIN = 7;
const int LOADCELL_DO5_PIN = 8;
const int LOADCELL_DO6_PIN = 9;
const int LOADCELL_SCK_PIN = 2;

int sensorPinArray[7] = { 3, 4, 5, 6, 7, 8, 9 };

HX711 sensorArray[7];

#define LIMIT_SWITCH 11
#define LED_PIN 13
#define ENABLE_PIN A1

ledObject led(LED_PIN);

//buttonObject tareButton(LIMIT_SWITCH, BUTTON_PULL_LOW);

autoDelay sampleDelay;

void testChannel(int channelNo) {
  Serial.print("Testing Channel: ");
  Serial.println(channelNo);
  Serial.print("  read: ");
  Serial.println(sensorArray[channelNo].read());  // print a raw reading from the ADC
  delay(500);
  Serial.print("  read average: ");
  Serial.println(sensorArray[channelNo].read_average(20));  // print the average of 20 readings from the ADC
  delay(500);
  Serial.print("  get value: ");
  Serial.println(sensorArray[channelNo].get_value(5));  // print the average of 5 readings from the ADC minus the tare weight
  delay(500);
  Serial.print("  get units: ");
  Serial.println(sensorArray[channelNo].get_units(5), 1);  // print the average of 5 readings from the ADC minus tare weight divided by the SCALE parameter
  delay(500);
}



void tareScale(int channel = 0) {
  Serial.println("Tare in 5 seconds... remove any weights from the sensorArray[i].");
  countdown(5);
  Serial.println("Taring...");
  countdown(5);
  sensorArray[channel].tare();  // Step 2
  Serial.println("Tare Complete..");
  delay(500);
}

void countdown(int from) {
  for (int i = from; i > 0; i--) {
    Serial.print(i);
    Serial.print("...");
    delay(1000);
  }
  Serial.println("0");
}



float scale_val;
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

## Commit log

2022-09-02 updated servo library to better reach 0 point -> 0 position not exactly 1ms pulse
2022-09-23 added calibration data for 8 trusses
2022-09-29 calibration data updated
2022-10-03 calibration data added for trus05
2022-10-06 added ability to set STARTUP state from serial, allowing recalibration without power cycle
2022-10-07 removed old calibration data
2023-06-06 Added all files for mini-truss-pcb
    #Note: Github link on the PCB says /minitruss but it felt better having that PCB design just part of this repo. Would it break anything to rename this minitruss at somepoint, or should I create a new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
    [MiniTruss.kicad_pcb, MiniTruss.kicad_sch, MiniTruss.sch, SN75175D.step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]
2023-06-06 Added the correct mini truss pcb folder
    [BOM_Truss_PCB.csv, BOM_Truss_PCB.xlsx, MiniTruss.kicad_pcb, MiniTruss.kicad_sch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]
2023-06-20 added basic firmware tests
    [bridge_driver0_sch.kicad_sch, load_cell.kicad_sch, micro_controller_sch.kicad_sch, power_distribution_sch.kicad_sch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]
